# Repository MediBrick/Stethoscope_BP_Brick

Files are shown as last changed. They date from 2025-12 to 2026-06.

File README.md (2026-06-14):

# Stethoscope with Pressure Sensor

<a href="./assets/pictures/Stethoscope_Front_Closed_with_Plugins.jpg" target="_blank" style="float: right; margin-left: 20px;">
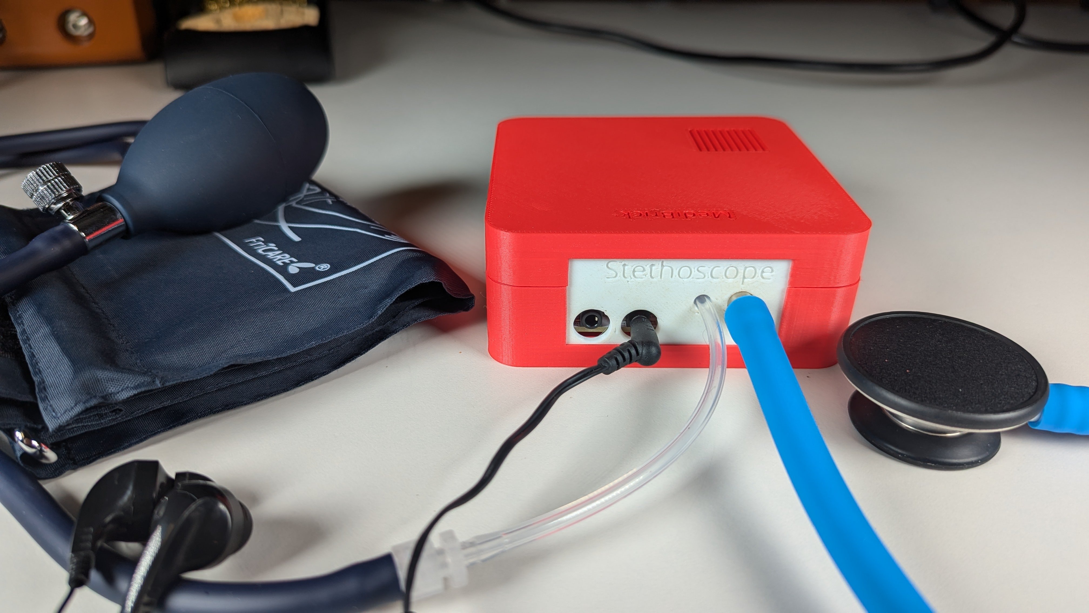
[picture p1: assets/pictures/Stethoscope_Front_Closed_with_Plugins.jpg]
  
</a>

The stethoscope and blood pressure brick consists of a sound as well as pressure recorder. For sound the I2S (Inter-Integrated Circuit Sound) bus is used to communicate with the microcontroller. This interface allows streaming and recording audio to an audio codec board. The Everest Semiconductor [ES8388 audio codec](datasheets/ES8388%20DS.pdf) was chosen because its supported by Arduino Audio Tools library and Arduino Audio Driver and because Espressif created the Lyrat Audio modules with published reference [designs](datasheets/esp32-lyrat-v4-schematic.pdf).

Sound was recorded with pui audio analog MEMS microphones [AMM-2742](datasheets/Microphone-AMM-2742-T-R.pdf) that are mounted on the printed circuit board.

However a new design is developed to use electret microphones that are attached to the flexible stethoscope tubing.

Two microphones are used where one is connected to the stethoscope and the other recording the background. An [dual differential amplifier](datasheets/opa344.pdf) is used to low pass filter and amplify the signal from the microphone, however amplification would not be needed for the ES8388 codec. Pressure is measured with a Honeywell MPR pressure sensor [MPRLS0300YG](datasheets/MPR_Pressure_HWSC_S_A0016036563_1-3073392.pdf) that convers the physiological range of 0 to 200 mm Hg.

## Costs &#36;

| Item        | Quantity at Purchase | Costs  | Source            | Cost per Brick
|---                          | ---  | ---    | ---               | ---
| Microcontroller             |  1   | $17.5  | [Adafruit](https://www.adafruit.com/product/5477)          | $17.5
| Display                     |  5   | $13    | [Amazon](https://a.co/d/1QH0Ab9)            | $3
| Button                      | 25   | $9     | [Amazon](https://a.co/d/8KAuTwC) | $0.5 
| Battery                     |  1   | $10     | [Adafruit](https://www.adafruit.com/product/258)        | $10
| PCB                         |  5   | $45.18 | PCBWay            | $9
| Parts and Assembly          |  2   | $56.55 | PCBWay            | $29
| MPRLS0300YG (pressure)      |  2   | $35    | [DigiKey](https://www.digikey.com/en/products/detail/honeywell-sensing-and-productivity-solutions/MPRLS0300YG00001B/10231660) | $17.5
| PUI AOM-5024L-HD-R (microphone)  |  2  | $4.2 | [Mouser](https://mou.sr/43AdqZY) | $8.4
| 3.5mm Audio jack stereo out(*)   | 1 | $0.9 | [Mouser](https://mou.sr/4uOWvy2) | $0.9
| 3.5mm Audio jacl mic in & stereo out(*) | 1 | $1.2 | [Mouser](https://mou.sr/4fyV8PS) | $1.2 |
| Stethoscope                 |  1   | $25    | [Amazon](https://a.co/d/7tQgoKs) | $25
| Arm Cuff                    |  1   | $17    | [Amazon](https://a.co/d/gKueGYV) | $17
| Assorted Wires              |8m    | $15    | [Amazon](https://a.co/d/58djefc) | $1
| Assorted Screws and Nuts    |100   |  $7    | Amazon            | $0.05
| Silocone Tubing             |  1   |  $9    | [Amazon](https://a.co/d/5GLJtFr) | $2
| Luer Lock female 3/32 barb  | 10   |  $9    | [Amazon](https://a.co/d/hxruOyw) | $1
| Luer Lock male 5/32 barb    | 10   |  $8    | [Amazon](https://a.co/d/c4cmtBQ) | $1
| Stainless Steel Tubing      |250mm | $10    | Amazon            | $2 |
| Assorted 3D printed parts   |      |        |                   | $3
|  **(*)** if not available at manufacturer, DIY |
| **Total with blood pressure**     |      |        |                   | **$140**
| **Total without blood pressure**  |      |        |                   | **$100**

Electronic components, excluding the pressure sensor, are $14 per board.

The pressure sensor was mounted in-house as the PCB assembly service did not have access to an inexpensive source.

## Software &#128187;

Main Program in Arduino folder:

- MediBrick_Stethoscope_BP_Microcontroller_Software: Refer to [Microcontroller_Software.md](Microcontroller_Software.md) for installation and usage instructions.

Test software is located in Arduino folder.

- MediBrick_Stethoscope_ES8388_to_CSV:
Prints the two-channel audio signal to the serial port for visualization with SerialUI application.

- MediBrick_Stethoscope_ES8388_TestSound: Creates test tone in left and right channels for headphones.

- MediBrick_Stethoscope_ES8388_to_Headphone: Plays the recorded sound to the headphone.

- MediBrick_Stethoscope_PressureTest: Test the arm cuff pressure sensor.

## Electronics Design &#128268;

<a href="KiCad/Sound_Schematic.pdf" target="_blank">
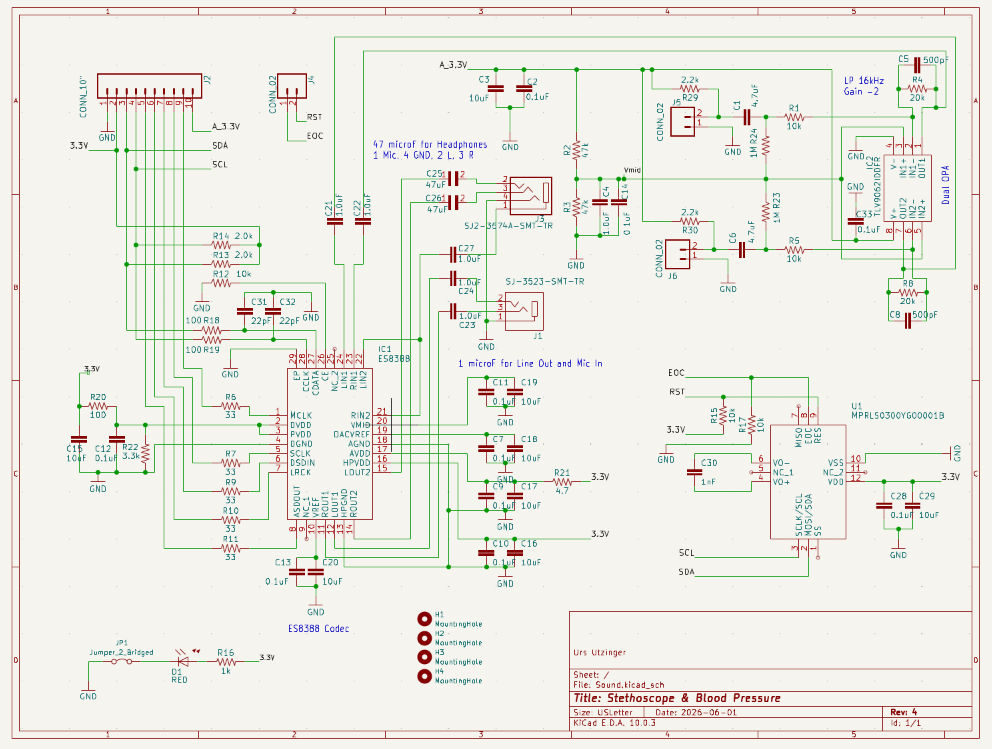
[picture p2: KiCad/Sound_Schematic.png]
  
</a>
<a href="KiCad/Sound_Layout.pdf" target="_blank">
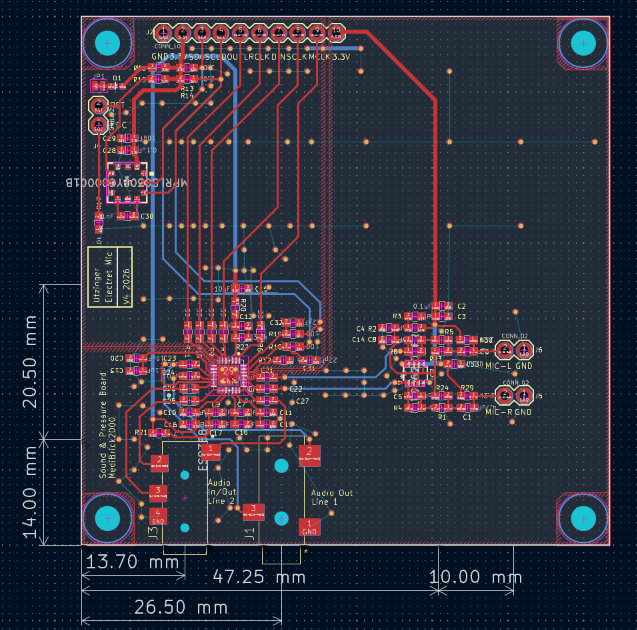
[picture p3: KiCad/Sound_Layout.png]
  
</a>

The following files are needed for PCB manufacturing and assembly at PCBWay.

- [Bill of Materials](KiCad/pcbway_production/2026-06-14-11-51-50/Sound.kicad_pcb_bom.csv)
- [Gerber Manufacturing Files](KiCad/pcbway_production/2026-06-14-11-51-50/Sound.kicad_pcb_gerber.zip)
- [Component Placement](KiCad/pcbway_production/2026-06-14-11-51-50/Sound.kicad_pcb_positions.csv)

The current design source is in [`KiCad`](KiCad/). The previous Eagle design is retained in [`Eagle`](Eagle/).

## 3D Printed Parts &#9881;
These are the links to the OnShape Design files, which you can edit and modify if you have an OnShape account (OnShape has free academic accounts).

- Microphone Housing
  - [Stethoscope Microphone Bottom](https://cad.onshape.com/documents/f23280f0a46d3d6c755669df/w/b75e085438cd92ba1b26b647/e/00c40c7437b1518e003bac9d)
  - [Stethoscope Microphone Top](https://cad.onshape.com/documents/ef2b037c38f1baa1c0b23c04/w/556b341c46d5852ab7c96559/e/758f32969c2d9c1e8976b746)

  <a href="Models/Assembly.jpg" target="_blank">
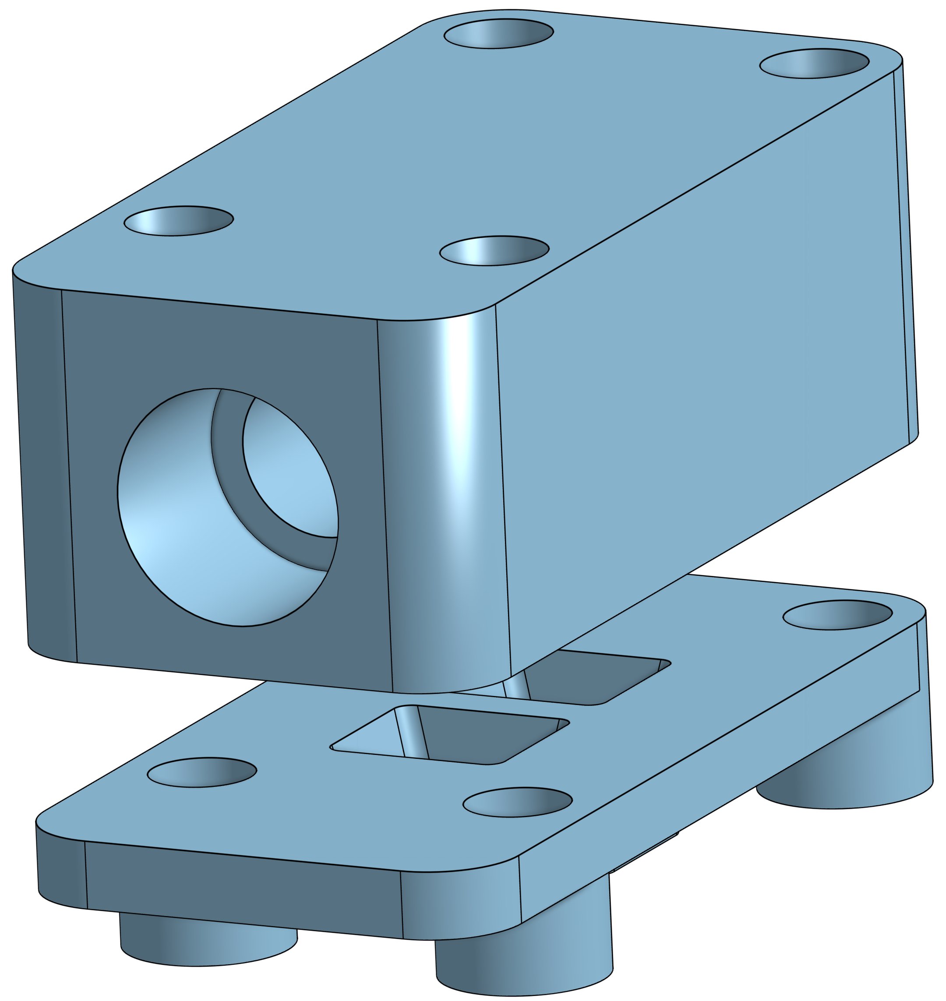
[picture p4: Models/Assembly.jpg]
    
  </a>

- MediBrick Casing (print each part separately) [This is not yet updated for new microphone]
  - [Brick Top/Board](https://cad.onshape.com/documents/ebcdcbc3e7eb802e05aa7127/w/92c7f2c4a3604ac0392e9e89/e/23d2cedb30284d3e07ce3fd7)
  - [Brick Bottom / Microcontroller](https://cad.onshape.com/documents/3fee40e68f3fb61ffdb812bb/w/65bb78ada38672d141a5d154/e/0ff82183503e2fd6c450e151)
  - [Stethoscope Interface Plate ](https://cad.onshape.com/documents/06546d5c2b6ecb0931149c5d/w/2aa54258cb58c3e795c7fea9/e/823e2851771a01788a8faacf)

## PCB Manufacturing Instructions &#128736;
When ordering at PCBWay:

Standard PCB
- Single pieces
- 70 x 70 mm
- 2 layers
- FR-4, TG 150-160
- Thickness 1.6 mm
- Minimum track width and spacing 0.15 mm
- Minimum through-hole diameter 0.25 mm
- No edge connectors
- Surface finish ENIG, 1U"
- Via process: Tenting Vias
- 1 oz Cu

Assembly Service
- Turnkey
- Single pieces
- Top side

Other Parameters
- Use the current BOM and component-placement files linked above for part counts
- Number of BGA/QFN parts: 1
- Through-hole connectors are installed separately

Customized Services and Advanced Options
- Leave as is

## Assembly Instructions &#128736;
  - [Assembly Instructions](./Assembly.md) 
 
## Audio Filters

The firmware provides adjustable high-pass and low-pass filters, software gain, and two-channel noise cancellation. These settings can be changed through the serial command interface described in [Microcontroller_Software.md](Microcontroller_Software.md).

The older offline filter-analysis utility remains available in [Compute_Filter_Coefficients.py](Compute_Filter_Coefficients.py).

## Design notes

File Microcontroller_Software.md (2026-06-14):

## Installation
Locate the "Arduino" folder in this repository. Download it to your computer. 

Install the following third-party libraries before compiling the software.

In the Arduino IDE, open `Sketch -> Include Library -> Manage Libraries...`, then search for and install each library listed below.

- [Adafruit BusIO](https://github.com/adafruit/Adafruit_BusIO)
- [Adafruit GFX Library](https://github.com/adafruit/Adafruit-GFX-Library)
- [Adafruit MAX1704X](https://github.com/adafruit/Adafruit_MAX1704X)
- [Adafruit MPRLS Library](https://github.com/adafruit/Adafruit_MPRLS)
- [Adafruit SSD1306](https://github.com/adafruit/Adafruit_SSD1306)

- Dependencies downloaded from pschatzmann, on his GitHub
  -  https://github.com/pschatzmann/arduino-audio-tools
  -  https://github.com/pschatzmann/arduino-audio-driver

Using the Arduino IDE, open the "MediBrick_Stethoscope_BP_Microcontroller_Software" folder, and flash the code to your ESP32-S3.

You will need to make sure the defaults for the wiring are correct.
It is recommended to select board configuration "USB Mode: CDC", "Upload Hardware CDC" and to enable "CDC on Boot".

## Usage Guide
The microcontroller software includes several built-in functions, including:

- Auto-shutoff after 4.5 hours
- Automatic zeroing of pressure when the MediBrick is turned on
- Blood pressure readings
- Stethoscope audio output
   - Headphone jack audio
   - SerialUI plotter

By default, the MediBrick operates in both blood pressure and stethoscope mode. In this mode, pressure readings are shown on the OLED display while stethoscope audio remains active. The stethoscope volume is set to 80% by default, and the SerialUI audio plot is disabled.

These settings can be adjusted through the internal serial menu. To access the menu guide, connect the MediBrick to the Arduino IDE through USB, open the Serial Monitor, and enter `h`. The Serial Monitor will then print the menu on the screen.

The following commands can be entered into the Serial Monitor:

**Mode selection**

| Command | Function |
|---|---|
| `p` | Pressure-only mode |
| `s` | Stethoscope-only mode |
| `b` | Both: pressure on OLED and audio active |

**Serial plot control** — while the plot is active, command responses are suppressed to keep the data stream clean

| Command | Function |
|---|---|
| `t` | Toggle audio plot on/off |
| `d` | Cycle plot decimation: 1 → 2 → 4 → 8 → 1 (reduces sample rate sent over serial) |
| `?` | Print help and turn plot off |
| `v` | Print all current settings and turn plot off |

**Settings persistence**

| Command | Function |
|---|---|
| `j` | Save current settings to flash |
| `J` | Load settings from flash and apply |

**Output (codec / headphone) volume** — range 0–100, step 6

| Command | Function |
|---|---|
| `>` | Output volume up |
| `<` | Output volume down |

**Input (microphone) volume** — nine discrete 3 dB gain levels

| Command | Function |
|---|---|
| `.` | Input volume up |
| `,` | Input volume down |

**Software gain** — range 0.5–4.0, step 0.5

| Command | Function |
|---|---|
| `+` | Software gain up |
| `-` | Software gain down |

**Low-pass filter** — step 250 Hz

| Command | Function |
|---|---|
| `L` | Low-pass cutoff frequency up |
| `l` | Low-pass cutoff frequency down |
| `K` | Low-pass filter ON |
| `k` | Low-pass filter OFF |

**High-pass filter** — step 1 Hz

| Command | Function |
|---|---|
| `H` | High-pass cutoff frequency up |
| `h` | High-pass cutoff frequency down |
| `G` | High-pass filter ON |
| `g` | High-pass filter OFF |

**Noise cancellation** (right channel minus scaled left channel)

| Command | Function |
|---|---|
| `N` | Noise cancel ON |
| `n` | Noise cancel OFF |
| `C` | Left noise scale up (step 0.05, range 0.5–1.5) |
| `c` | Left noise scale down (step 0.05, range 0.5–1.5) |

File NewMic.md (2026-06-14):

# Microphones

## Electret

- Primo EM272Z1 80 SNR -28dB 60-20000 10mm $17
- Primo EM272J  80 SNR -28dB 60-20000 10mm 600uA $17 digikey
- Primo EM258   75 SNR -32dB 60-20000 5.8mm $4.73
- Primo EM281   71 SNR -39dB 30-20000 5.8mm 450 uA $8.24 digikey
- PUI AUM-4538L 60 SNR -38dB 20-20000 9.7mm 450 uA $3 digikey

** PUI AOM-5024L-HD-R 80 SNR -24dB 20-20000 10mm (4mm opening) $4.2 **

## MEMS
differential, needs differential amp (Adafruit reference design)

- Infineon       IM70A135  70 SNR -38dB 37-20000 170uA $2.25
- TDK/InvenSense ICS-40638 63 SNR -43dB 35-20000 170uA $3.41 digikey

## Current MEMS
- PUI         AMM-2742-T-R 59 SNR -42dB 20-20000 $1.8 digikey

## Circuit for New PUI AOM-5024L-HD-R or PUI AOM-5024L-HD-F-R

### Microphone Connection
```
3.3V_Analog
  |
  2.2k
  |
  +--------- MIC+
  |
  +--------- audio out node
            |
           Ccouple 4.7 -10 uF
            |
           next stage

MIC- ---------------- AGND
```

### Direct connection (not used)
```
Electret bias node
      |
      Ccouple
   4.7–10 µF
      |
     470-1k
      |
      +-------- ES8388 LIN/RIN
      |
     1 nF (470-2.2nF)
      |
     AGND
```

### With Non Inverting OpAmp (not used)

```
3.3V_A
  |
 47k
  |
  +-----+----+- Vmid ≈ 1.65 V
  |     |    |
 47k  1-10uF 100nF
  |     |    |
 AGND   AGND AGND

Electret bias node
      |
   Ccouple
     4.7 µF
      |
      +---- 10k ----> Op Amp +IN
                    |
                    1M
                    |
                   Vmid

                 Rf
OpAmp OUT -----/\/\/\-----+
                          |
                        OpAmp -IN
                          |
                 Rg       |
Vmid ----------/\/\/\-----+

Gain = 1 + Rf/Rg

2× gain:  Rf = 10 kΩ, Rg = 10 kΩ
5× gain:  Rf = 39 kΩ, Rg = 10 kΩ
10× gain: Rf = 90 kΩ, Rg = 10 kΩ
```
## With Inverting OpAmp (used)

### Bias
```
3.3V_A
  |
 47k
  |
  +-----+----+- Vmid ≈ 1.65 V
  |     |    |
 47k  1-10uF 100nF
  |     |    |
 AGND   AGND AGND
```
### Electret microphone bias
```
3.3V_A
  |
 2.2k
  |
  +-------- Electret Mic +
  |
  +-------- Electret bias / signal node
```
### Coupling into inverting input
```
Electret bias / signal node
      |
   Ccouple
   4.7 µF
      |
      +---- Rin ----> Op Amp -IN

Op Amp +IN --------> Vmid
```

Optional bleed/startup resistor:

```
Node after Ccouple
      |
      1M
      |
     Vmid
```

### Fedback

```
                 Rf
OpAmp OUT -----/\/\/\-----+
                 ||       |
                 Cf       |
                 ||       |
                        OpAmp -IN
                          |
                 Rin      |
Mic signal ----/\/\/\-----+

Gain = -Rf / Rin

1× gain:   Rf = 10 kΩ,   Rin = 10 kΩ
2× gain:   Rf = 22 kΩ,   Rin = 10 kΩ **
5× gain:   Rf = 49.9 kΩ, Rin = 10 kΩ
10× gain:  Rf = 100 kΩ,  Rin = 10 kΩ

Rf = 10 kΩ,   Cf = 1 nF   → fc ≈ 15.9 kHz **
Rf = 22 kΩ,   Cf = 1 nF   → fc ≈ 7.2 kHz
Rf = 49.9 kΩ, Cf = 470 pF → fc ≈ 6.8 kHz
```

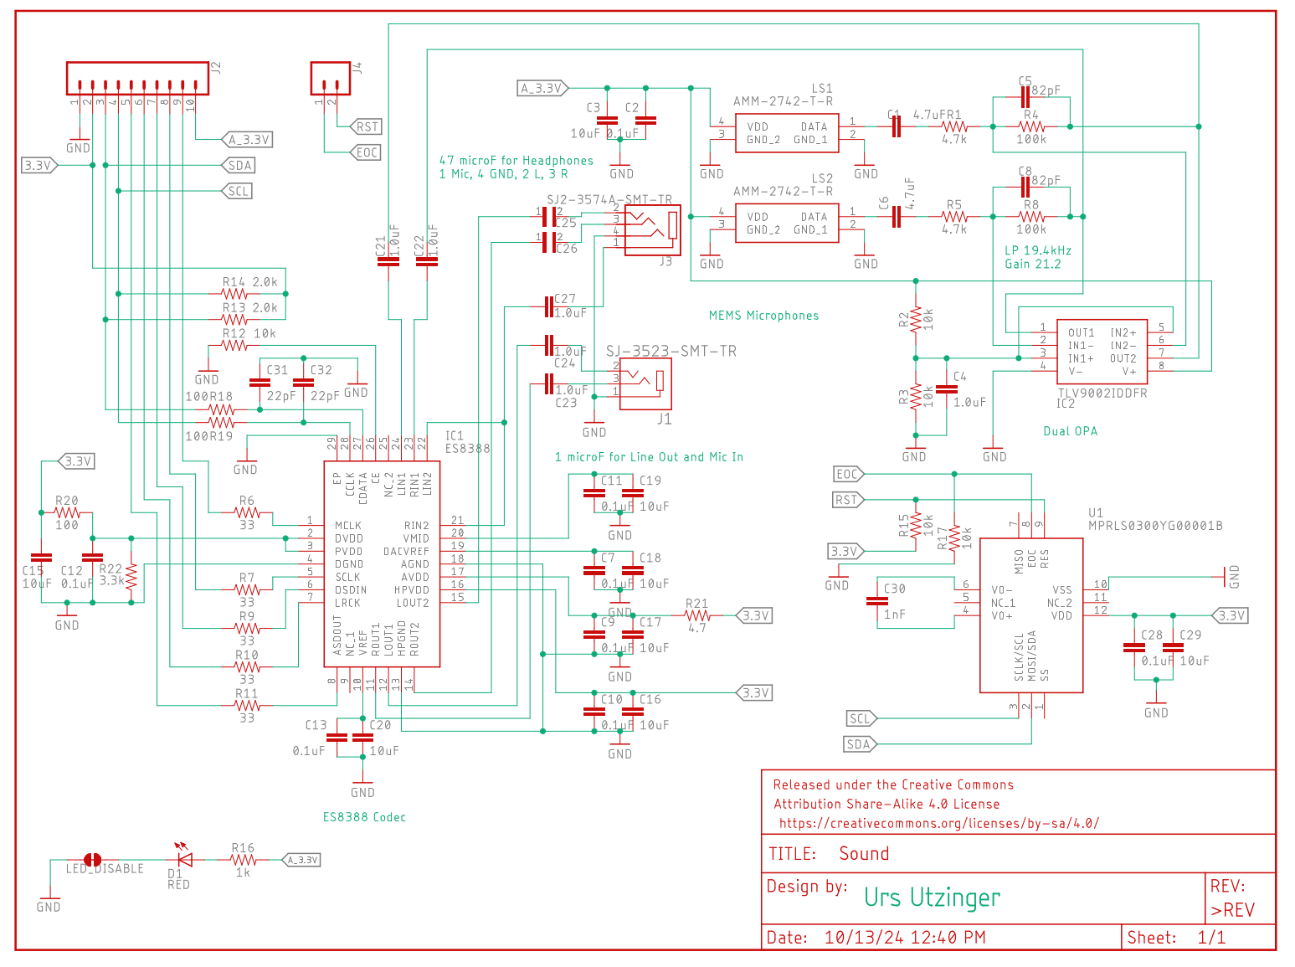
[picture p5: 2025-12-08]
Eagle/Sound_schematic.png

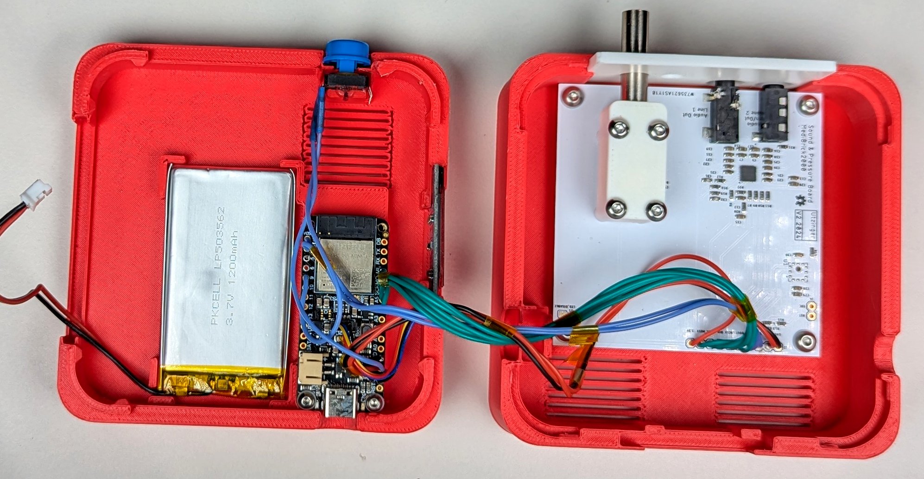
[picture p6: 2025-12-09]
assets/pictures/Stethoscope_Top_Open_without_Plugins.jpg

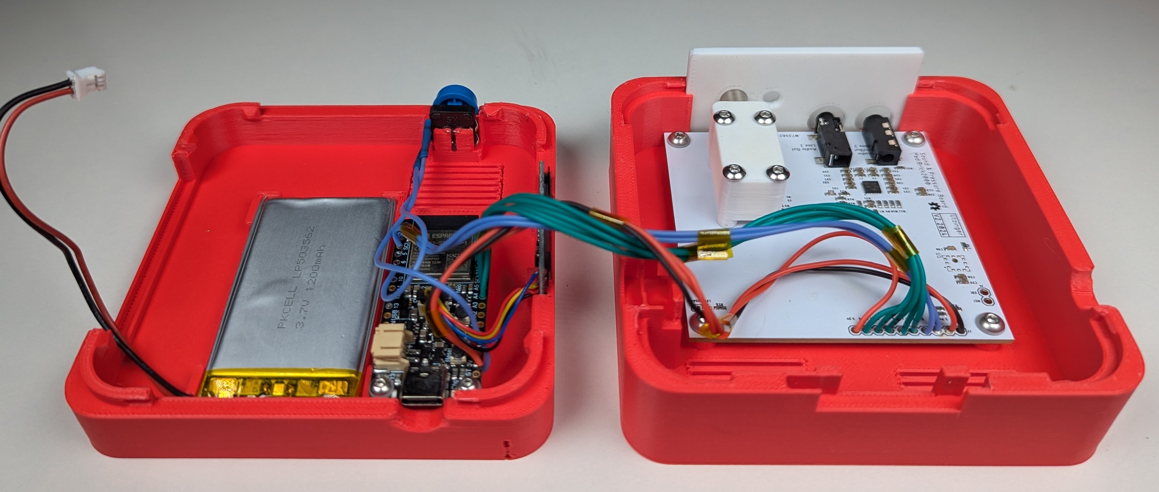
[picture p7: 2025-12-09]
assets/pictures/Stethoscope_Front_Open_without_Plugins.jpg

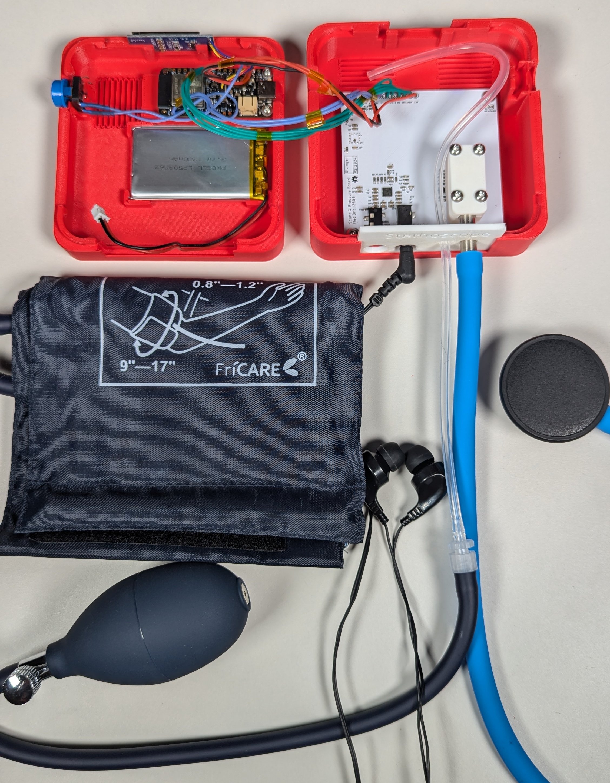
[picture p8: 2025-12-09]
assets/pictures/Stethoscope_Top_Open_with_Plugins_2.jpg

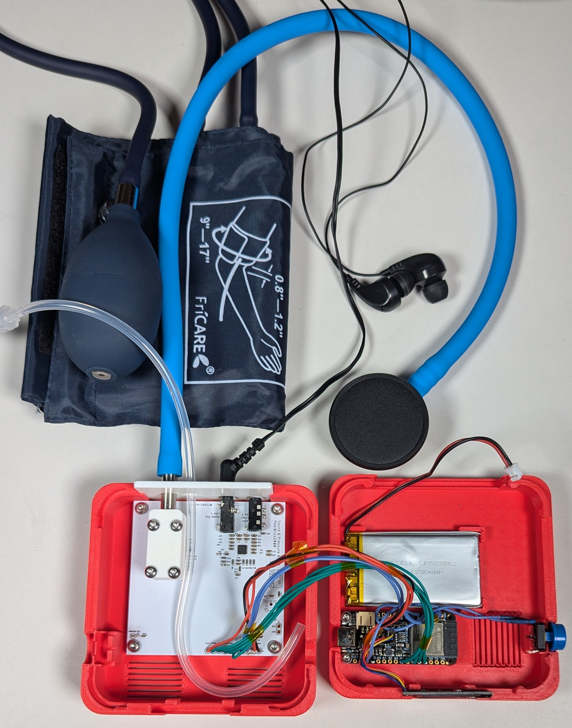
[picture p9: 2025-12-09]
assets/pictures/Stethoscope_Top_Open_with_Plugins.jpg

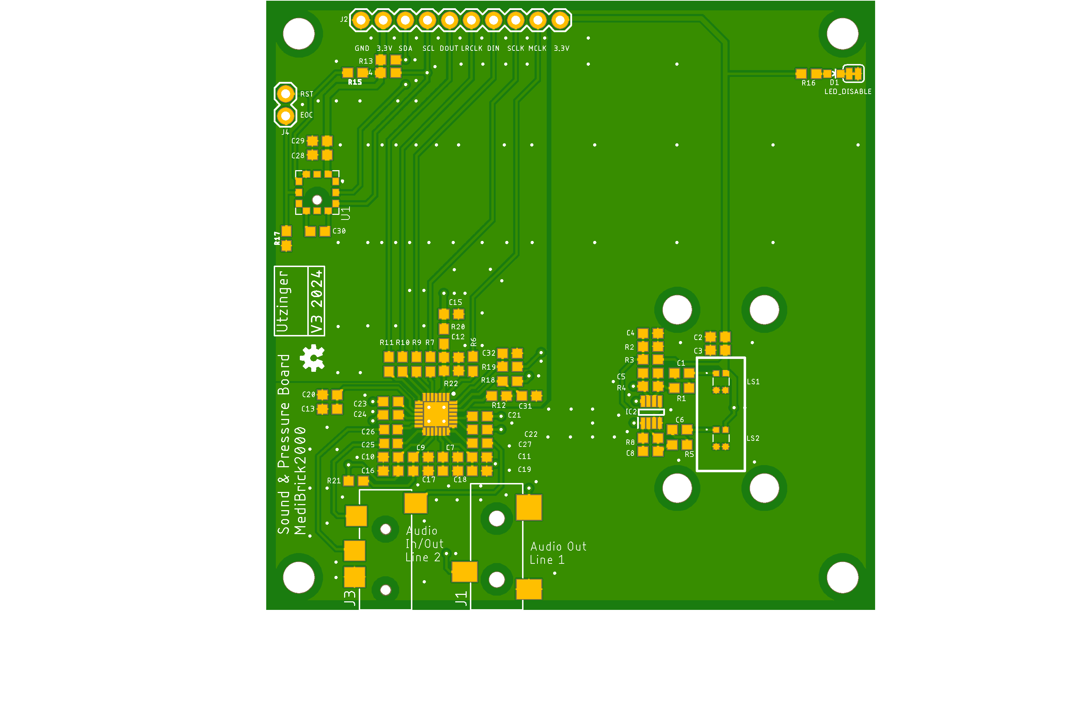
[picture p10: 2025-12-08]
Eagle/Sound_top.png

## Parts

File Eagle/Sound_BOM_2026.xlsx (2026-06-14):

Based on PCBWay Bom Quotation
Item # | *Designator | *Qty | Manufacturer | *Mfg Part # | Description / Value | Vendor Part # | *Package/Footprint | Mounting Type | Your Instructions / Notes | *Unit Price(2 sets) | *Total | *Delivery Time | *Actual Purchase Mfg Part # | Customer Reply
1 | C2, C7, C9, C10, C11, C12, C13, C28 | 8 | muRata | GRM188R71H104KA93D | 0.1uF | C77055 | 0603 | SMD |  |  | $0.000
2 | C4, C21, C22, C23, C24, C27 | 6 | muRata | GCM188R71E105KA64D | 1.0uF | C85862 | 0603 | SMD |  |  | $0.000
3 | C3, C15, C16, C17, C18, C19, C20, C29 | 8 | muRata | GRM188R61A106KE69D | 10uF | C77044 | 0603 | SMD |  |  | $0.000
4 | C1, C6 | 2 | muRata | GRM188R61E475KE11D | 4.7uF | C90057 | 0603 | SMD |  |  | $0.000
5 | C5, C8 | 2 | muRata | GCM1885C2A181JA16D | 180pF | C440148 | 0603 | SMD |  |  | $0.000
6 | C25, C26 | 2 | muRata | GRM188R60J476ME15D | 47uF | C140782 | 0603 | SMD |  |  | $0.000
7 | C30 | 1 | muRata | GRM1885C1H102JA01D | 1nF | C77026 | 0603 | SMD |  |  | $0.000
8 | C31, C32 | 2 | muRata | GCG1885G1H220JA01D | 22pF | C3884601 | 0603 | SMD |  |  | $0.000
9 | R1, R5 | 2 | YAGEO | RC0603FR-074K7L | 4.7k | C99782 | 0603 | SMD |  |  | $0.000
10 | R2, R3, R12, R15, R17 | 5 | YAGEO | RT0603BRD0710KL | 10k | C95204 | 0603 | SMD |  |  | $0.000
11 | R4, R8 | 2 | YAGEO | RC0603JR-0747KL | 47k | C127447 | 0603 | SMD |  |  | $0.000
12 | R6, R7, R9, R10, R11 | 5 | YAGEO | RC0603JR-0733RL | 33 | C108407 | 0603 | SMD |  |  | $0.000
13 | R13, R14 | 2 | YAGEO | RT0603BRB072KL | 2k | C326555 | 0603 | SMD |  |  | $0.000 |  | RC0603FR-072KL
14 | R16 | 1 | YAGEO | RT0603BRD071KL | 1k | C110776 | 0603 | SMD |  |  | $0.000
15 | R18, R19, R20 | 3 | YAGEO | RT0603BRD07100RL | 100 | C122970 | 0603 | SMD |  |  | $0.000
16 | R21 | 1 | YAGEO | RT0603DRE074R7L | 4.7 | C863140 | 0603 | SMD |  |  | $0.000
17 | R22 | 1 | YAGEO | RT0603BRB073K3L | 3.3k | C860369 | 0603 | SMD |  |  | $0.000
18 | LS1, LS2 | 2 | PUI Audio, Inc. | AMM-2742-T-R | AMM-2742-T-R, MEMS Microphones |  | 0603 | SMD | https://mou.sr/4uW6BxI |  | $0.000 | 7-10 Workdays
19 | IC1 | 1 | Everest-semi(Everest Semiconductor) | ES8388 | ES8388 | C365736 | QFN-28-EP(4x4) | SMD |  |  | $0.000
20 | D1 | 1 | XINGLIGHT | XL-1608UBC-04 | Blue LED | C965807 | 0603 | SMD |  |  | $0.000
21 | J1 | 1 | CUI Devices | SJ-3523-SMT-TR | SJ-3523-SMT-TR, 3.5mm Audio Jack | C4991872 |  | SMD | https://mou.sr/4uOWvy2 |  | $0.000
22 | J3 | 1 | CUI Devices | SJ2-3574A-SMT-TR | SJ2-3574A-SMT-TR, 3.5mm Audio Jack with microphone | C4991637 |  | SMD | https://mou.sr/4fyV8PS |  | $0.000 | 7-10 Workdays
23 | IC2 | 1 | Texas Instruments | TLV9062IDDFR | 10 MHz, RRIO, CMOS operational amplifier | C2867884 | TSOT-23-8 | SMD |  |  | $0.000 | 7-10 Workdays
 |  |  |  |  |  |  |  |  |  | Component Cost | $0.00

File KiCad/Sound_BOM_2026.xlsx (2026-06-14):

Item # | *Designator | *Qty | Manufacturer | *Mfg Part # | Description / Value | Vendor Part # | *Package/Footprint | Mounting Type | Your Instructions / Notes | *Unit Price(2 sets) | *Total | *Delivery Time | *Actual Purchase Mfg Part # | Customer Reply
1 | C2, C7, C9, C10, C11, C12, C13, C14, C28, C33 | 10 | muRata | GRM188R71H104KA93D | 100nF | C77055 | 0603 | SMD |  |  | $0.000
2 | C4, C21, C22, C23, C24, C27 | 6 | muRata | GCM188R71E105KA64D | 1.0uF | C85862 | 0603 | SMD |  |  | $0.000
3 | C3, C15, C16, C17, C18, C19, C20, C29 | 8 | muRata | GRM188R61A106KE69D | 10uF | C77044 | 0603 | SMD |  |  | $0.000
4 | C1, C6 | 2 | muRata | GRM188R61E475KE11D | 4.7uF | C90057 | 0603 | SMD |  |  | $0.000
5 | C5, C8 | 2 | YAEGO | CC0603JRNPO9BN501 | 500pF | C3879676 | 0603 | SMD |  |  | $0.000
6 | C25, C26 | 2 | muRata | GRM188R60J476ME15D | 47uF | C140782 | 0603 | SMD |  |  | $0.000
7 | C30 | 1 | muRata | GRM1885C1H102JA01D | 1nF | C77026 | 0603 | SMD |  |  | $0.000
8 | C31, C32 | 2 | muRata | GCG1885G1H220JA01D | 22pF | C3884601 | 0603 | SMD |  |  | $0.000
9 | R1, R5, R12, R15, R17 | 5 | YAGEO | RT0603BRD0710KL | 10k | C95204 | 0603 | SMD |  |  | $0.000
10 | R2, R3 | 2 | YAGEO | RC0603JR-0747KL | 47k | C127447 | 0603 | SMD |  |  | $0.000
11 | R4, R8 | 2 | YAGEO | RT0603BRD0720KL | 20k | C723637 | 0603 | SMD |  |  | $0.000
12 | R6, R7, R9, R10, R11 | 5 | YAGEO | RC0603JR-0733RL | 33 | C108407 | 0603 | SMD |  |  | $0.000
13 | R13, R14 | 2 | YAGEO | RT0603BRB072KL | 2k | C326555 | 0603 | SMD |  |  | $0.000 |  | RC0603FR-072KL
14 | R16 | 1 | YAGEO | RT0603BRD071KL | 1k | C110776 | 0603 | SMD |  |  | $0.000
15 | R18, R19, R20 | 3 | YAGEO | RT0603BRD07100RL | 100 | C122970 | 0603 | SMD |  |  | $0.000
16 | R21 | 1 | YAGEO | RT0603DRE074R7L | 4.7 | C863140 | 0603 | SMD |  |  | $0.000
17 | R22 | 1 | YAGEO | RT0603BRB073K3L | 3.3k | C860369 | 0603 | SMD |  |  | $0.000
18 | R23, R24 | 2 | YAGEO | RC0603FR-071ML | 1M | C105578 | 0603 | SMD
19 | R29, R30 | 2 | YAGEO | AC0603FR-072K2L | 2.2k | C125931 | 0603 | SMD
20 | IC1 | 1 | Everest-semi(Everest Semiconductor) | ES8388 | ES8388 | C365736 | QFN-28-EP(4x4) | SMD |  |  | $0.000
21 | D1 | 1 | XINGLIGHT | XL-1608UBC-04 | Blue LED | C965807 | 0603 | SMD |  |  | $0.000
22 | J1 | 1 | CUI Devices | SJ-3523-SMT-TR | SJ-3523-SMT-TR, 3.5mm Audio Jack | C4991872 | Custom | SMD | https://mou.sr/4uOWvy2 |  | $0.000
23 | J2 | 1 |  | Connector | 1x10 | Do not populate
24 | J3 | 1 | CUI Devices | SJ2-3574A-SMT-TR | SJ2-3574A-SMT-TR, 3.5mm Audio Jack with microphone | C4991637 | Custom | SMD | https://mou.sr/4fyV8PS |  | $0.000 | 7-10 Workdays
25 | J4, J5, J6 | 3 |  | Connector | 1x2 | Do not populate
26 | JP1 | 1 |  | Jumper NC |  | Do not populate
27 | IC2 | 1 | Texas Instruments | TLV9062IDDFR | 10 MHz, RRIO, CMOS operational amplifier | C2867884 | TSOT-23-8 | SMD |  |  | $0.000 | 7-10 Workdays
 |  |  |  |  |  |  |  |  |  | Component Cost | $0.00
 |  | 69

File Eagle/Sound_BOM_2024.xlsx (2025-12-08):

Item # | Designator | Qty | Manufacturer | Mfg Part # | LCSC Part# | U.S. Distributor | Description / Value | *Package/Footprint | Mounting Type | Your Instructions / Notes
1 | C2, C7, C9, C10, C11, C12, C13, C28 | 8 | Samsung Electro-Mechanics (https://www.lcsc.com/brand-detail/254.html) | CL10B104KA8NNNC (https://www.lcsc.com/product-detail/Multilayer-Ceramic-Capacitors-MLCC-SMD-SMT_Samsung-Electro-Mechanics-CL10B104KA8NNNC_C1590.html) | C1590 (https://www.lcsc.com/product-detail/Multilayer-Ceramic-Capacitors-MLCC-SMD-SMT_Samsung-Electro-Mechanics-CL10B104KA8NNNC_C1590.html) |  | 0.1uF | 0603 | SMD
2 | C4, C21, C22, C23, C24, C27 | 6 | Samsung Electro-Mechanics (https://www.lcsc.com/brand-detail/254.html) | CL10A105KA8NNNC (https://www.lcsc.com/product-detail/Multilayer-Ceramic-Capacitors-MLCC-SMD-SMT_Samsung-Electro-Mechanics-CL10A105KA8NNNC_C5673.html) | C5673 (https://www.lcsc.com/product-detail/Multilayer-Ceramic-Capacitors-MLCC-SMD-SMT_Samsung-Electro-Mechanics-CL10A105KA8NNNC_C5673.html) |  | 1.0uF | 0603 | SMD
3 | C3, C15, C16, C17, C18, C19, C20, C29 | 8 | Samsung Electro-Mechanics (https://www.lcsc.com/brand-detail/254.html) | CL10A106MA8NRNC (https://www.lcsc.com/product-detail/Multilayer-Ceramic-Capacitors-MLCC-SMD-SMT_Samsung-Electro-Mechanics-CL10A106MA8NRNC_C96446.html) | C96446 (https://www.lcsc.com/product-detail/Multilayer-Ceramic-Capacitors-MLCC-SMD-SMT_Samsung-Electro-Mechanics-CL10A106MA8NRNC_C96446.html) |  | 10uF | 0603 | SMD
4 | C1, C6 | 2 | Samsung Electro-Mechanics (https://www.lcsc.com/brand-detail/254.html) | CL10A475KA8NQNC (https://www.lcsc.com/product-detail/Multilayer-Ceramic-Capacitors-MLCC-SMD-SMT_Samsung-Electro-Mechanics-CL10A475KA8NQNC_C69335.html) | C69335 (https://www.lcsc.com/product-detail/Multilayer-Ceramic-Capacitors-MLCC-SMD-SMT_Samsung-Electro-Mechanics-CL10A475KA8NQNC_C69335.html) |  | 4.7uF | 0603 | SMD
5 | C5, C8 | 2 | Samsung Electro-Mechanics (https://www.lcsc.com/brand-detail/254.html) | CL10C102JB8NNNC (https://www.lcsc.com/product-detail/Multilayer-Ceramic-Capacitors-MLCC-SMD-SMT_Samsung-Electro-Mechanics-CL10C102JB8NNNC_C163508.html) | C163508 (https://www.lcsc.com/product-detail/Multilayer-Ceramic-Capacitors-MLCC-SMD-SMT_Samsung-Electro-Mechanics-CL10C102JB8NNNC_C163508.html) |  | 1000pF | 0603 | SMD | Was 82.pF in version 2
6 | C25, C26 | 2 | Samsung Electro-Mechanics (https://www.lcsc.com/brand-detail/254.html) | CL10A476MQ8QRNC (https://www.lcsc.com/product-detail/Multilayer-Ceramic-Capacitors-MLCC-SMD-SMT_Samsung-Electro-Mechanics-CL10A476MQ8QRNC_C730416.html) | C730416 (https://www.lcsc.com/product-detail/Multilayer-Ceramic-Capacitors-MLCC-SMD-SMT_Samsung-Electro-Mechanics-CL10A476MQ8QRNC_C730416.html) |  | 47uF | 0603 | SMD
7 | C30 | 1 | Samsung Electro-Mechanics (https://www.lcsc.com/brand-detail/254.html) | CL10B102KB8NNNC (https://www.lcsc.com/product-detail/Multilayer-Ceramic-Capacitors-MLCC-SMD-SMT_Samsung-Electro-Mechanics-CL10B102KB8NNNC_C1588.html) | C1588 (https://www.lcsc.com/product-detail/Multilayer-Ceramic-Capacitors-MLCC-SMD-SMT_Samsung-Electro-Mechanics-CL10B102KB8NNNC_C1588.html) |  | 1nF | 0603 | SMD
8 | C31, C32 | 2 | Samsung Electro-Mechanics (https://www.lcsc.com/brand-detail/254.html) | CL10C220JB8NNNC (https://www.lcsc.com/product-detail/Multilayer-Ceramic-Capacitors-MLCC-SMD-SMT_Samsung-Electro-Mechanics-CL10C220JB8NNNC_C1653.html) | C1653 (https://www.lcsc.com/product-detail/Multilayer-Ceramic-Capacitors-MLCC-SMD-SMT_Samsung-Electro-Mechanics-CL10C220JB8NNNC_C1653.html) |  | 22pF | 0603 | SMD
9 | R1, R5 | 2 | YAGEO (https://www.lcsc.com/brand-detail/396.html) | RC0603FR-074K7L (https://www.lcsc.com/product-detail/Chip-Resistor-Surface-Mount_YAGEO-RC0603FR-074K7L_C99782.html) | C99782 (https://www.lcsc.com/product-detail/Chip-Resistor-Surface-Mount_YAGEO-RC0603FR-074K7L_C99782.html) |  | 4.7k | 0603 | SMD
10 | R2, R3, R12, R15, R17 | 5 | YAGEO (https://www.lcsc.com/brand-detail/396.html) | RC0603FR-0710KL (https://www.lcsc.com/product-detail/Chip-Resistor-Surface-Mount_YAGEO-RC0603FR-0710KL_C98220.html) | C98220 (https://www.lcsc.com/product-detail/Chip-Resistor-Surface-Mount_YAGEO-RC0603FR-0710KL_C98220.html) |  | 10k | 0603 | SMD
11 | R4, R8 | 2 | YAGEO (https://www.lcsc.com/brand-detail/396.html) | RC0603FR-078K2L (https://www.lcsc.com/product-detail/Chip-Resistor-Surface-Mount_YAGEO-RC0603FR-078K2L_C114637.html) | C114637 (https://www.lcsc.com/product-detail/Chip-Resistor-Surface-Mount_YAGEO-RC0603FR-078K2L_C114637.html) |  | 8.2k | 0603 | SMD | Was 100k in version 2
12 | R6, R7, R9, R10, R11 | 5 | YAGEO (https://www.lcsc.com/brand-detail/396.html) | RC0603FR-0733RL (https://www.lcsc.com/product-detail/Chip-Resistor-Surface-Mount_YAGEO-RC0603FR-0733RL_C108661.html) | C108661 (https://www.lcsc.com/product-detail/Chip-Resistor-Surface-Mount_YAGEO-RC0603FR-0733RL_C108661.html) |  | 33 | 0603 | SMD
13 | R13, R14 | 2 | YAGEO (https://www.lcsc.com/brand-detail/396.html) | RC0603FR-072KL (https://www.lcsc.com/product-detail/Chip-Resistor-Surface-Mount_YAGEO-RC0603FR-072KL_C105576.html) | C105576 (https://www.lcsc.com/product-detail/Chip-Resistor-Surface-Mount_YAGEO-RC0603FR-072KL_C105576.html) |  | 2k | 0603 | SMD
14 | R16 | 1 | YAGEO (https://www.lcsc.com/brand-detail/396.html) | RC0603FR-071KL (https://www.lcsc.com/product-detail/Chip-Resistor-Surface-Mount_YAGEO-RC0603FR-071KL_C22548.html) | C22548 (https://www.lcsc.com/product-detail/Chip-Resistor-Surface-Mount_YAGEO-RC0603FR-071KL_C22548.html) |  | 1k | 0603 | SMD
15 | R18, R19, R20 | 3 | YAGEO (https://www.lcsc.com/brand-detail/396.html) | RC0603FR-07100RL (https://www.lcsc.com/product-detail/Chip-Resistor-Surface-Mount_YAGEO-RC0603FR-07100RL_C105588.html) | C105588 (https://www.lcsc.com/product-detail/Chip-Resistor-Surface-Mount_YAGEO-RC0603FR-07100RL_C105588.html) |  | 100 | 0603 | SMD
16 | R21 | 1 | YAGEO (https://www.lcsc.com/brand-detail/396.html) | RC0603FR-074R7L (https://www.lcsc.com/product-detail/Chip-Resistor-Surface-Mount_YAGEO-RC0603FR-074R7L_C137705.html) | C137705 (https://www.lcsc.com/product-detail/Chip-Resistor-Surface-Mount_YAGEO-RC0603FR-074R7L_C137705.html) |  | 4.7 | 0603 | SMD
17 | R22 | 1 | YAGEO (https://www.lcsc.com/brand-detail/396.html) | RC0603FR-073K3L (https://www.lcsc.com/product-detail/Chip-Resistor-Surface-Mount_YAGEO-RC0603FR-073K3L_C108078.html) | C108078 (https://www.lcsc.com/product-detail/Chip-Resistor-Surface-Mount_YAGEO-RC0603FR-073K3L_C108078.html) |  | 3.3k | 0603 | SMD
18 | LS1, LS2 | 2 | PUI Audio, Inc. (https://www.lcsc.com/brand-detail/13209.html) | AMM-2742-T-R (https://www.lcsc.com/product-detail/MEMS-Microphones_PUI-Audio-Inc-AMM-2742-T-R_C3171735.html) | C3171735 (https://www.lcsc.com/product-detail/MEMS-Microphones_PUI-Audio-Inc-AMM-2742-T-R_C3171735.html) | https://www.mouser.com/ProductDetail/PUI-Audio/AMM-2742-T-R?qs=zhx2xqPtQQyJoGop0O%252BpMA%3D%3D | AMM-2742-T-R, MEMS Microphones | 0603 | SMD
19 | IC1 | 1 | Everest-semi(Everest Semiconductor) (https://www.lcsc.com/brand-detail/11902.html) | ES8388 (https://www.lcsc.com/product-detail/ADCs-DACs-Special-Purpose_Everest-semi-Everest-Semiconductor-ES8388_C365736.html) | C365736 (https://www.lcsc.com/product-detail/ADCs-DACs-Special-Purpose_Everest-semi-Everest-Semiconductor-ES8388_C365736.html) |  | ES8388 | QFN-28-EP(4x4) | SMD
20 | D1 | 1 | XINGLIGHT | XL-1608UBC-04 (https://www.lcsc.com/product-detail/Light-Emitting-Diodes-LED_XINGLIGHT-XL-1608UBC-04_C965807.html) | C965807 (https://www.lcsc.com/product-detail/Light-Emitting-Diodes-LED_XINGLIGHT-XL-1608UBC-04_C965807.html) |  | Blue LED | 0603 | SMD
21 | J1 | 1 | CUI Devices (https://www.lcsc.com/brand-detail/15740.html) | SJ-3523-SMT-TR (https://www.lcsc.com/product-detail/Audio-Connector-Headphone_CUI-Devices-SJ-3523-SMT-TR_C4991872.html) |  | https://www.mouser.com/ProductDetail/CUI-Devices/SJ-3523-SMT-TR?qs=WyjlAZoYn51zOHzJ3r4ZRA%3D%3D | SJ-3523-SMT-TR, 3.5mm Audio Jack |  | SMD
22 | J3 | 1 | CUI Devices (https://www.lcsc.com/brand-detail/15740.html) | SJ2-3574A-SMT-TR (https://www.lcsc.com/product-detail/Audio-Connector-Headphone_CUI-Devices-SJ2-3574A-SMT-TR_C4991637.html) |  | https://www.mouser.com/ProductDetail/CUI-Devices/SJ2-3574A-SMT-TR?qs=DXv0QSHKF4zeQKpjIMxQnA%3D%3D | SJ2-3574A-SMT-TR, 3.5mm Audio Jack with microphone |  | SMD
23 | IC2 | 1 | Texas Instruments (https://www.lcsc.com/brand-detail/100.html) | TLV9002IDDFR (https://www.lcsc.com/product-detail/Operational-Amplifier_Texas-Instruments-TLV9002IDDFR_C2862620.html) | C2862620 (https://www.lcsc.com/product-detail/Operational-Amplifier_Texas-Instruments-TLV9002IDDFR_C2862620.html) |  | TLV9002IDDFR, Dual OpAmp | TSOT-23-8 | SMD
 |  | 60
 | Resistors | 22
 | Capacitors | 31

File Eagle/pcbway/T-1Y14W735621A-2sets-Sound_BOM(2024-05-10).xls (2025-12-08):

PCBWay Bom Quotation, Product No.:T-1Y14W735621A
Item # | *Designator | *Qty | Manufacturer | *Mfg Part # | Description / Value | Vendor Part # | *Package/Footprint | Mounting Type | Your Instructions / Notes | *Unit Price(2 sets) | *Total | *Delivery Time | *PCBWay Note | Customer Reply
1 | C2, C7, C9, C10, C11, C12, C13, C28 | 8 | Samsung Electro-Mechanics | CL10B104KA8NNNC | 0.1uF | C1590 | 0603 | SMD |  | $0.024 | $0.384
2 | C4, C21, C22, C23, C24, C27 | 6 | Samsung Electro-Mechanics | CL10A105KA8NNNC | 1.0uF | C5673 | 0603 | SMD |  | $0.042 | $0.504
3 | C3, C14, C15, C16, C17, C18, C19, C20, C29 | 9 | Samsung Electro-Mechanics | CL10A106MA8NRNC | 10uF | C96446 | 0603 | SMD |  | $0.042 | $0.756
4 | C1, C6 | 2 | Samsung Electro-Mechanics | CL10A475KA8NQNC | 4.7uF | C69335 | 0603 | SMD |  | $0.063 | $0.252
5 | C5, C8 | 2 | Samsung Electro-Mechanics | CL10C270JB81PNC | 27pF | C346211 | 0603 | SMD |  | $0.063 | $0.252
6 | C25, C26 | 2 | Samsung Electro-Mechanics | CL10A476MQ8QRNC | 47uF | C730416 | 0603 | SMD |  | $0.258 | $1.032
7 | C30 | 1 | Samsung Electro-Mechanics | CL10B102KB8NNNC | 1nF | C1588 | 0603 | SMD |  | $0.126 | $0.252
8 | R1, R5 | 2 | YAGEO | RC0603FR-074K7L | 4.7k | C99782 | 0603 | SMD |  | $0.035 | $0.140
9 | R2, R3, R12, R13, R14 | 5 | YAGEO | RC0603FR-0710KL | 10k | C98220 | 0603 | SMD |  | $0.013 | $0.130
10 | R4, R8 | 2 | YAGEO | RC0603FR-07300KL | 300k | C114667 | 0603 | SMD |  | $0.039 | $0.156
11 | R6, R7, R9, R10, R11, R15, R17 | 7 | YAGEO | RC0603FR-0733RL | 33 | C108661 | 0603 | SMD |  | $0.011 | $0.154
12 | R16 | 1 | YAGEO | RC0603FR-071KL | 1k | C22548 | 0603 | SMD |  | $0.065 | $0.130
13 | LS1, LS2 | 2 | PUI Audio, Inc. | AMM-2742-T-R | AMM-2742-T-R, MEMS Microphones | C3171735 | 0603 | SMD | https://www.mouser.com/ProductDetail/PUI-Audio/AMM-2742-T-R?qs=zhx2xqPtQQyJoGop0O%252BpMA%3D%3D | $2.537 | $10.148 | 7-10 Workdays | Only 270pcs total in stock, please confirm ASAP.
14 | IC1 | 1 | Everest-semi(Everest Semiconductor) | ES8388 | ES8388 | C365736 | QFN-28-EP(4x4) | SMD |  | $1.464 | $2.928
15 | U1 | 1 | Honeywell | MPRLS0300YG00001BB | MPRLS0300YG00001B |  |  | SMD | https://www.mouser.com/ProductDetail/Honeywell/MPRLS0300YG00001B?qs=MLItCLRbWszf0bln%252B%2FiVCQ%3D%3D | $67.882 | $135.764 | 7-10 Workdays | Only 400pcs total in stock, please confirm ASAP.
16 | D1 | 1 | XINGLIGHT | XL-1608UBC-04 | Blue LED | C965807 | 0603 | SMD |  | $0.238 | $0.476
17 | J1 | 1 | CUI Devices | SJ-3523-SMT-TR | SJ-3523-SMT-TR, 3.5mm Audio Jack |  |  | SMD | https://www.mouser.com/ProductDetail/CUI-Devices/SJ-3523-SMT-TR?qs=WyjlAZoYn51zOHzJ3r4ZRA%3D%3D | $2.113 | $4.226
18 | J3 | 1 | CUI Devices | SJ2-3574A-SMT-TR | SJ2-3574A-SMT-TR, 3.5mm Audio Jack with microphone |  |  | SMD | https://www.mouser.com/ProductDetail/CUI-Devices/SJ2-3574A-SMT-TR?qs=DXv0QSHKF4zeQKpjIMxQnA%3D%3D | $1.916 | $3.832 | 7-10 Workdays
19 | IC2 | 1 | Texas Instruments | TLV9002IDDFR | TLV9002IDDFR, Dual OpAmp | C2862620 | TSOT-23-8 | SMD |  | $1.057 | $2.114
 |  |  |  |  |  |  |  |  |  | Component Cost | $163.63

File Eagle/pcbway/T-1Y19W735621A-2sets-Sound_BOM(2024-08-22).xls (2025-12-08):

PCBWay Bom Quotation, Product No.:T-1Y19W735621A
Item # | *Designator | *Qty | Manufacturer | *Mfg Part # | Description / Value | Vendor Part # | *Package/Footprint | Mounting Type | Your Instructions / Notes | *Unit Price(2 sets) | *Total | *Delivery Time | *Actual Purchase Mfg Part # | Customer Reply
1 | C2, C7, C9, C10, C11, C12, C13, C28 | 8 | Samsung Electro-Mechanics | CL10B104KA8NNNC | 0.1uF | C1590 | 0603 | SMD |  | $0.026 | $0.416
2 | C4, C21, C22, C23, C24, C27 | 6 | Samsung Electro-Mechanics | CL10A105KA8NNNC | 1.0uF | C5673 | 0603 | SMD |  | $0.010 | $0.120
3 | C3, C15, C16, C17, C18, C19, C20, C29 | 8 | Samsung Electro-Mechanics | CL10A106MA8NRNC | 10uF | C96446 | 0603 | SMD |  | $0.041 | $0.656
4 | C1, C6 | 2 | Samsung Electro-Mechanics | CL10A475KA8NQNC | 4.7uF | C69335 | 0603 | SMD |  | $0.063 | $0.252
5 | C5, C8 | 2 | Samsung Electro-Mechanics | CL10C820JB81PNC | 82pF | C472802 | 0603 | SMD |  | $0.063 | $0.252
6 | C25, C26 | 2 | Samsung Electro-Mechanics | CL10A476MQ8QRNC | 47uF | C730416 | 0603 | SMD |  | $0.184 | $0.736
7 | C30 | 1 | Samsung Electro-Mechanics | CL10B102KB8NNNC | 1nF | C1588 | 0603 | SMD |  | $0.126 | $0.252
8 | C31, C32 | 2 | Samsung Electro-Mechanics | CL10C220JB8NNNC | 22pF | C1653 | 0603 | SMD |  | $0.063 | $0.252
9 | R1, R5 | 2 | YAGEO | RC0603FR-074K7L | 4.7k | C99782 | 0603 | SMD |  | $0.053 | $0.212
10 | R2, R3, R12, R15, R17 | 5 | YAGEO | RC0603FR-0710KL | 10k | C98220 | 0603 | SMD |  | $0.013 | $0.130
11 | R4, R8 | 2 | YAGEO | RC0603FR-07100KL | 100k | C14675 | 0603 | SMD |  | $0.031 | $0.124
12 | R6, R7, R9, R10, R11 | 5 | YAGEO | RC0603FR-0733RL | 33 | C108661 | 0603 | SMD |  | $0.016 | $0.160
13 | R13, R14 | 2 | YAGEO | RC0603FR-0710KL | 2k | C98220 | 0603 | SMD |  | $0.038 | $0.152 |  | RC0603FR-072KL
14 | R16 | 1 | YAGEO | RC0603FR-071KL | 1k | C22548 | 0603 | SMD |  | $0.063 | $0.126
15 | R18, R19, R20 | 3 | YAGEO | RC0603FR-07100RL | 100 | C105588 | 0603 | SMD |  | $0.021 | $0.126
16 | R21 | 1 | YAGEO | RC0603FR-074R7L | 4.7 | C137705 | 0603 | SMD |  | $0.105 | $0.210
17 | R22 | 1 | YAGEO | RC0603FR-073K3L | 3.3k | C108078 | 0603 | SMD |  | $0.078 | $0.156
18 | LS1, LS2 | 2 | PUI Audio, Inc. | AMM-2742-T-R | AMM-2742-T-R, MEMS Microphones | C3171735 | 0603 | SMD | https://www.mouser.com/ProductDetail/PUI-Audio/AMM-2742-T-R?qs=zhx2xqPtQQyJoGop0O%252BpMA%3D%3D | $2.507 | $10.028 | 7-10 Workdays
19 | IC1 | 1 | Everest-semi(Everest Semiconductor) | ES8388 | ES8388 | C365736 | QFN-28-EP(4x4) | SMD |  | $1.464 | $2.928
20 | D1 | 1 | XINGLIGHT | XL-1608UBC-04 | Blue LED | C965807 | 0603 | SMD |  | $0.215 | $0.430
21 | J1 | 1 | CUI Devices | SJ-3523-SMT-TR | SJ-3523-SMT-TR, 3.5mm Audio Jack |  |  | SMD | https://www.mouser.com/ProductDetail/CUI-Devices/SJ-3523-SMT-TR?qs=WyjlAZoYn51zOHzJ3r4ZRA%3D%3D | $2.113 | $4.226
22 | J3 | 1 | CUI Devices | SJ2-3574A-SMT-TR | SJ2-3574A-SMT-TR, 3.5mm Audio Jack with microphone |  |  | SMD | https://www.mouser.com/ProductDetail/CUI-Devices/SJ2-3574A-SMT-TR?qs=DXv0QSHKF4zeQKpjIMxQnA%3D%3D | $1.916 | $3.832 | 7-10 Workdays
23 | IC2 | 1 | Texas Instruments | TLV9002IDDFR | TLV9002IDDFR, Dual OpAmp | C2862620 | TSOT-23-8 | SMD |  | $0.887 | $1.774 | 7-10 Workdays
 |  |  |  |  |  |  |  |  |  | Component Cost | $27.55

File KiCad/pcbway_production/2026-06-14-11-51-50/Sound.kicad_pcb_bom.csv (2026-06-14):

Designator | Quantity | Value | Footprint | Package | MPN | DNP | Mount_Type | Description
C1, C6 | 2 | 4.7uF | 0603 |  |  |  | smt
C10, C11, C12, C13, C14, C2, C28, C33, C7, C9 | 10 | 0.1uF | 0603 |  |  |  | smt
C15, C16, C17, C18, C19, C20, C29, C3 | 8 | 10uF | 0603 |  |  |  | smt
C21, C22, C23, C24, C27, C4 | 6 | 1.0uF | 0603 |  |  |  | smt
C25, C26 | 2 | 47uF | CAPC1608X100N |  |  |  | smt
C30 | 1 | 1nF | 0603 |  |  |  | smt
C31, C32 | 2 | 22pF | 0603 |  |  |  | smt
C5, C8 | 2 | 500pF | 0603 |  |  |  | smt
D1 | 1 | RED | LED-0603 |  |  |  | smt
IC1 | 1 | ES8388 | QFN45P400X400X80-29N |  |  |  | smt
IC2 | 1 | TLV9062IDDFR | SOT_62IDDFR_TEX-L |  |  |  | smt
J1 | 1 | SJ-3523-SMT-TR | CUI_SJ-3523-SMT-TR |  |  |  | smt
J2 | 1 | CONN_10" | 1X10 |  |  |  | tht
J3 | 1 | SJ2-3574A-SMT-TR | CUI_SJ2-3574A-SMT-TR |  |  |  | smt
J4, J5, J6 | 3 | CONN_02 | 1X02 |  |  |  | tht
JP1 | 1 | Jumper_2_Bridged | Jumper_2_NC_Trace_NoSilk |  |  |  | smt | Jumper, 2-pole, closed/bridged
R1, R12, R15, R17, R5 | 5 | 10k | 0603 |  |  |  | smt
R10, R11, R6, R7, R9 | 5 | 33 | 0603 |  |  |  | smt
R13, R14 | 2 | 2.0k | 0603 |  |  |  | smt
R16 | 1 | 1k | 0603 |  |  |  | smt
R18, R19, R20 | 3 | 100 | 0603 |  |  |  | smt
R2, R3 | 2 | 47k | 0603 |  |  |  | smt
R21 | 1 | 4.7 | 0603 |  |  |  | smt
R22 | 1 | 3.3k | 0603 |  |  |  | smt
R23, R24 | 2 | 1M | 0603 |  |  |  | smt
R29, R30 | 2 | 2.2k | 0603 |  |  |  | smt
R4, R8 | 2 | 20k | 0603 |  |  |  | smt
U1 | 1 | MPRLS0300YG00001B | MPRLS0300YG00001B_HNW |  |  |  | smt

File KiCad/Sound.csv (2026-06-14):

Id | Designator | Footprint | Quantity | Designation | Supplier and ref
1 | C1, C6 | 0603 | 2 | 4.7uF
2 | C2, C7, C9, C10, C11, C12, C13, C14, C28, C33 | 0603 | 10 | 0.1uF
3 | C3, C15, C16, C17, C18, C19, C20, C29 | 0603 | 8 | 10uF
4 | C4, C21, C22, C23, C24, C27 | 0603 | 6 | 1.0uF
5 | C5, C8 | 0603 | 2 | 500pF
6 | C25, C26 | CAPC1608X100N | 2 | 47uF
7 | C30 | 0603 | 1 | 1nF
8 | C31, C32 | 0603 | 2 | 22pF
9 | D1 | LED-0603 | 1 | RED
10 | IC1 | QFN45P400X400X80-29N | 1 | ES8388
11 | IC2 | SOT_62IDDFR_TEX-L | 1 | TLV9062IDDFR
12 | J1 | CUI_SJ-3523-SMT-TR | 1 | SJ-3523-SMT-TR
13 | J2 | 1X10 | 1 | CONN_10";;; 14;J3" | CUI_SJ2-3574A-SMT-TR | 1 | SJ2-3574A-SMT-TR
15 | J4, J5, J6 | 1X02 | 3 | CONN_02
16 | JP1 | Jumper_2_NC_Trace_NoSilk | 1 | Jumper_2_Bridged
17 | R1, R5, R12, R15, R17 | 0603 | 5 | 10k
18 | R2, R3 | 0603 | 2 | 47k
19 | R4, R8 | 0603 | 2 | 20k
20 | R6, R7, R9, R10, R11 | 0603 | 5 | 33
21 | R13, R14 | 0603 | 2 | 2.0k
22 | R16 | 0603 | 1 | 1k
23 | R18, R19, R20 | 0603 | 3 | 100
24 | R21 | 0603 | 1 | 4.7
25 | R22 | 0603 | 1 | 3.3k
26 | R23, R24 | 0603 | 2 | 1M
27 | R29, R30 | 0603 | 2 | 2.2k
28 | U1 | MPRLS0300YG00001B_HNW | 1 | MPRLS0300YG00001B

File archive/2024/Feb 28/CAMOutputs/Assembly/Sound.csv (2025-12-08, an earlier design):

Qty | Value | Device | Package | Parts | Description | DESCRIPTION | DESIGNER | HEIGHT | MANUFACTURER_NAME | MANUFACTURER_PART_NUMBER | MOUSER_PART_NUMBER | MOUSER_PRICE-STOCK | PROD_ID | VALUE | VERSION
1 |  | CONN_06SILK_FEMALE_PTH | 1X06 | J3 | Multi connection point. Often used as Generic Header-pin footprint for 0.1 inch spaced/style header connections |  |  |  |  |  |  |  | CONN-08437
1 |  | CONN_10";1X10" | J2 | Multi connection point. Often used as Generic Header-pin footprint for 0.1 inch spaced/style header connections |  |  |  |  |  |  |  | CONN-11563
1 |  | ES8388ES8388 | ES8388 | J1 | ES8388 PCBArtists Breakout Board
1 | 0.1uF | 0.1UF-0603-25V-(+80/-20%) | 0603 | C3 | 0.1µF ceramic capacitors |  |  |  |  |  |  |  | CAP-00810 | 0.1uF
1 | 1.0uF | 1.0UF-0603-16V-10% | 0603 | C4 | 1µF ceramic capacitors |  |  |  |  |  |  |  | CAP-00868 | 1.0uF
2 | 10k | 10KOHM-0603-1/10W-1% | 0603 | R2, R3 | 10kΩ resistor |  |  |  |  |  |  |  | RES-00824 | 10k
1 | 10uF | 10UF-0603-6.3V-20% | 0603 | C2 | 10.0µF ceramic capacitors |  |  |  |  |  |  |  | CAP-11015 | 10uF
1 | 1k | 1KOHM-0603-1/10W-1% | 0603 | R16 | 1kΩ resistor |  |  |  |  |  |  |  | RES-07856 | 1k
2 | 27pF | 27PF-0603-50V-5% | 0603 | C5, C8 | 27pF ceramic capacitors |  |  |  |  |  |  |  | CAP-09989 | 27pF
2 | 300k | 300KOHM-0603-1/10W-1% | 0603 | R4, R8 | 300kΩ resistor |  |  |  |  |  |  |  | RES-10809 | 300k
2 | 4.7k | 4.7KOHM-0603-1/10W-1% | 0603 | R1, R5 | 4.7kΩ resistor |  |  |  |  |  |  |  | RES-07857 | 4.7k
2 | 4.7uF | 4.7UF0603 | 0603 | C1, C6 | 4.7µF ceramic capacitors |  |  |  |  |  |  |  | CAP-08280 | 4.7uF
2 | AMM-2742-T-R | AMM-2742-T-R | AMM2742TR | LS1, LS2 | Microphones MICROPHONE OMNI -42 DB 2VDC 150uA | Microphones MICROPHONE OMNI -42 DB 2VDC 150uA |  | 0.9mm | PUI Audio | AMM-2742-T-R | 665-AMM-2742-T-R | https://www.mouser.co.uk/ProductDetail/PUI-Audio/AMM-2742-T-R?qs=zhx2xqPtQQyJoGop0O%252BpMA%3D%3D
1 | FRAME-LETTERNO_PACKAGE | FRAME-LETTERNO_PACKAGE | DUMMY | FRAME1 | Schematic Frame - Letter |  | Nobody |  |  |  |  |  |  |  | v01
1 | JUMPER-SMT_2_NC_TRACE_SILK | JUMPER-SMT_2_NC_TRACE_SILK | SMT-JUMPER_2_NC_TRACE_SILK | LED_DISABLE | Normally closed trace jumper
2 | OPA344 | OPA344 | SOT23-5 | U$1, U$2 | Single gate rail-to-rail output op-amp. Inputs extend 300mV past rails. |  |  |  |  |  |  |  | IC-08251 | OPA344
1 | RED | LED-RED0603 | LED-0603 | D1 | Assorted Red LEDs |  |  |  |  |  |  |  | DIO-00819 | RED

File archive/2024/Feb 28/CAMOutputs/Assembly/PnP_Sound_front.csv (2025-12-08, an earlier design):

C1 | 52.75 | 27.25 | 180.00 | 4.7uF | 0603
C2 | 56.90 | 31.40 | 180.00 | 10uF | 0603
C3 | 56.90 | 29.85 | 180.00 | 0.1uF | 0603
C4 | 48.50 | 32.50 | 0.00 | 1.0uF | 0603
C5 | 48.35 | 22.50 | 180.00 | 27pF | 0603
C6 | 52.50 | 20.75 | 180.00 | 4.7uF | 0603
C8 | 48.35 | 16.00 | 180.00 | 27pF | 0603
D1 | 10.75 | 7.25 | 180.00 | RED | LED-0603
LED_DISABLE | 10.75 | 5.00 | 90.00 | JUMPER-SMT_2_NC_TRACE_SILK | SMT-JUMPER_2_NC_TRACE_SILK
LS1 | 57.25 | 26.25 | 0.00 | AMM-2742-T-R | AMM2742TR
LS2 | 57.25 | 19.75 | 0.00 | AMM-2742-T-R | AMM2742TR
R1 | 52.75 | 25.50 | 180.00 | 4.7k | 0603
R16 | 10.75 | 10.25 | 90.00 | 1k | 0603
R2 | 48.50 | 29.50 | 0.00 | 10k | 0603
R3 | 48.50 | 31.00 | 180.00 | 10k | 0603
R4 | 48.35 | 24.05 | 180.00 | 300k | 0603
R5 | 52.50 | 19.00 | 180.00 | 4.7k | 0603
R8 | 48.35 | 17.50 | 180.00 | 300k | 0603
U$1 | 48.50 | 26.50 | 270.00 | OPA344 | SOT23-5
U$2 | 48.50 | 19.95 | 270.00 | OPA344 | SOT23-5

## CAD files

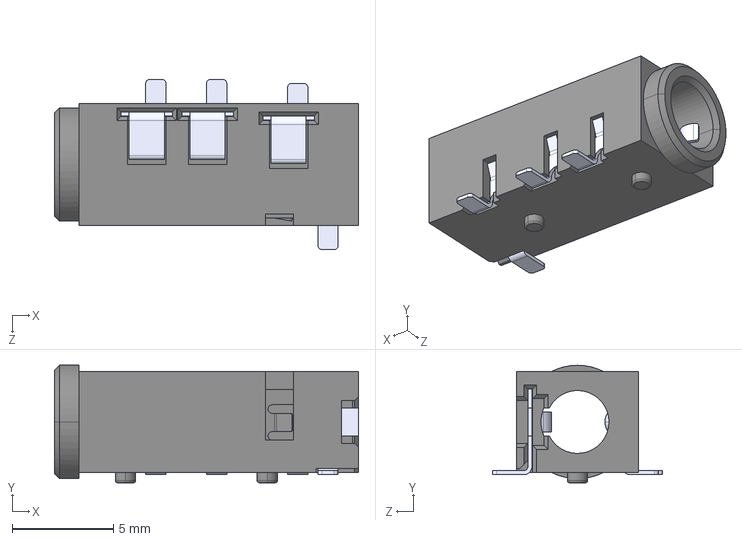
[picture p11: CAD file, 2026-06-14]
KiCad/Sound.3d/SJ2-3574A-SMT-TR--3DModel-STEP-56544.STEP
15.0 x 5.80 x 8.40 mm

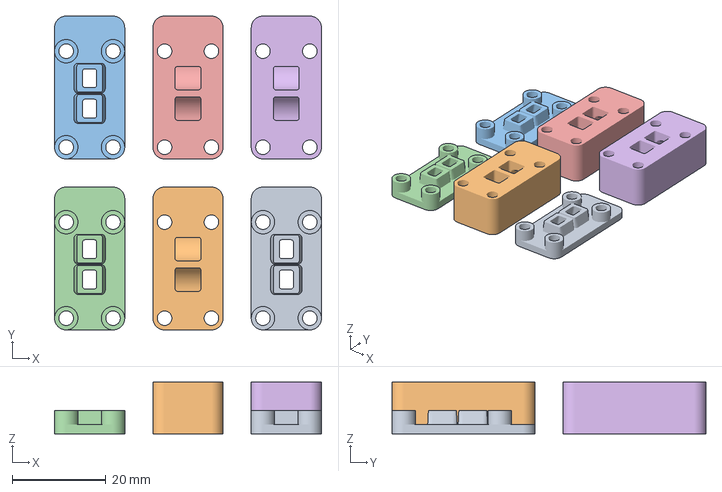
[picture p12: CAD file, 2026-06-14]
Models/MicrophoneHousing.3mf
57.0 x 67.0 x 11.0 mm
MicrophoneBottom.stl x 3
MicrophoneTop.stl x 3

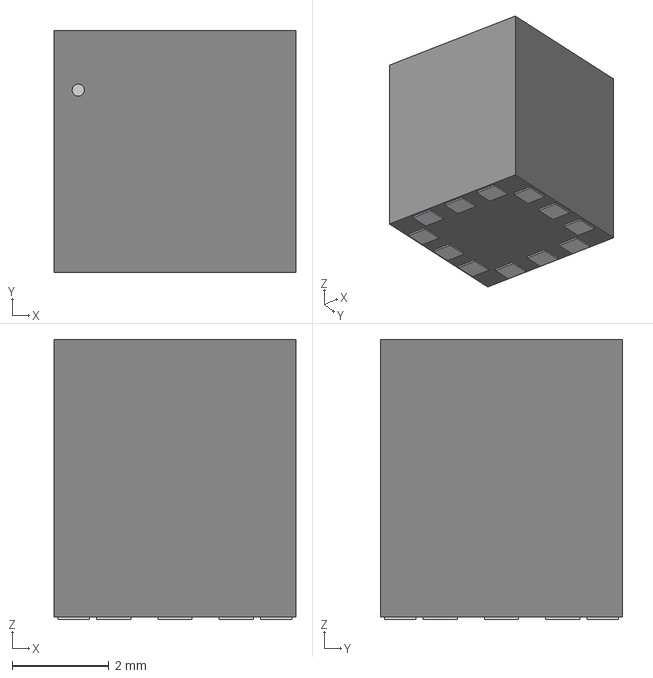
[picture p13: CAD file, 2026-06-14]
KiCad/Sound.3d/MPRLS0300YG00001B_HNW.step
5.00 x 5.00 x 5.79 mm

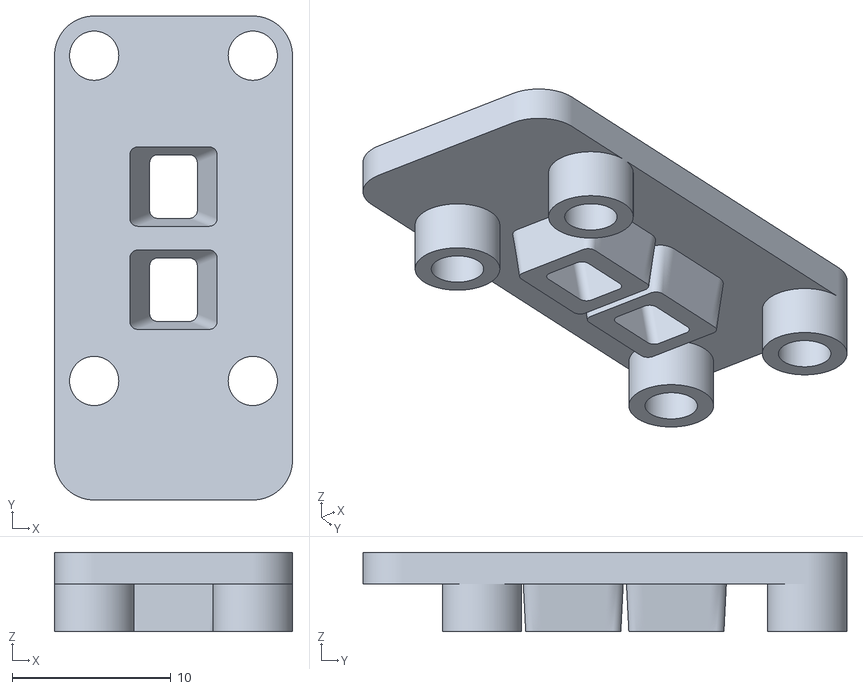
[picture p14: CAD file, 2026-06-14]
Models/MicrophoneBottom.stl
15.0 x 30.5 x 5.00

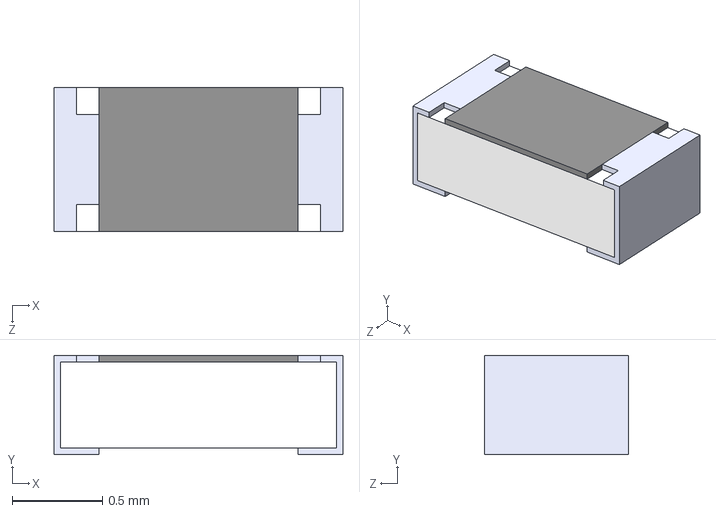
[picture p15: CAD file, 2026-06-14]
KiCad/Sound.3d/RC0603FR-07220RL.STEP
1.60 x 0.55 x 0.8 mm

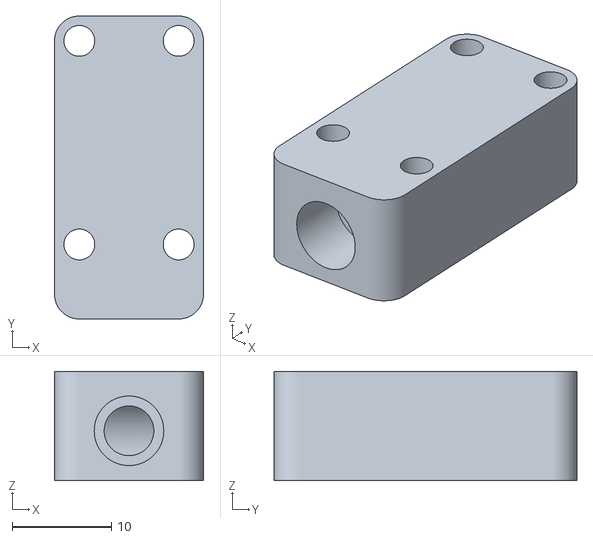
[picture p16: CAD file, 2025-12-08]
Models/MicrophoneTop.stl
15.0 x 30.5 x 11.0

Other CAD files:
KiCad/Sound.3d/MPRLS0300YG00001B_HNW.stl

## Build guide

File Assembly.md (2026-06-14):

# Assembly of Stethoscope & Blood Pressure MediBrick

## Required Parts

- Fully assembled Stethoscope PCB
- Microcontroller board:
  - Adafruit Feather ESP32-S3, or
  - SparkFun Thing Plus C
- Honeywell MPRLS0300YG pressure sensor
- OLED display
- Pushbutton
- Battery
- AWG 22 or AWG 24 silicone wire
- Stainless steel tubing, 7 mm OD, 5 mm ID
- Stethoscope chest piece and tubing
- Inflatable arm cuff
- Silicone tubing
- Luer lock adapters
- Miscellaneous hardware:
  - M3 screws, 20 mm, and nuts for PCB mounting
  - M3 & M2.5 screws for microcontroller / enclosure mounting
  - Plastic washers

## 3D Printed Parts

For the design models, refer to the README.

- MediBrick Outer Casing
  - Outer casing top part
  - Outer casing bottom part
- Microphone Housing
  - Microphone housing has not been updated yet for new 10mm microphones.
- Side plate

## Tubing and Adapter Notes

- Suggested stethoscope rubber tube: **5 mm ID**, using a barb with **8 mm OD**
- Suggested pressure cuff tube: **4 mm ID**, using a barb with **7 mm OD**
- Rubber tubing from Honeywell pressure sensor to arm cuff: **2 mm ID, 4 mm OD**
- Luer Lock **3/32** barbed adapter for rubber tubing from pressure sensor
- Luer Lock **5/32** barbed adapter for pressure cuff tube

## Required Tools

- Soldering iron
- Hot-air rework station
- Solder
- Flux
- Tweezers
- Isopropyl alcohol
- Small screwdrivers
- Wire cutters / wire strippers
- Continuity tester or multimeter

---

# Assembly Procedure

## 1. Collect and inspect all parts

Verify that all electrical, mechanical, and tubing components are present before beginning assembly. Inspect the PCB, 3D-printed parts, and microcontroller board for visible damage or manufacturing defects.

## 2. Solder the pressure sensor to the PCB

Use a hot-air rework station to solder the **Honeywell MPRLS0300YG** pressure sensor to the board. For ease of soldering, also heat the assembled board with a [miniture hot plate from Adafruit](https://www.adafruit.com/product/4948) or [from AliExpress](https://www.aliexpress.us/item/3256806194378309.html)

1. Locate the pressure sensor footprint on the PCB. The solder pads form a square pattern.
2. Identify the orientation marker on the PCB footprint. One corner of the footprint has a dot.
3. Apply flux to the pressure sensor pads on the PCB. A generous amount of flux is acceptable.
4. Inspect the underside of the pressure sensor and locate its orientation dot.
5. Place the pressure sensor onto the PCB footprint, aligning the dot on the sensor with the dot on the PCB.
6. Set the hotplate to approximately **200 °C**.
7. Set the hot-air station to approximately **350 °C**.
8. Let the temperature of the hotplate increase.
9. Using gentle airflow, heat the pressure sensor evenly from above until the solder reflows and the sensor settles into place.
10. Do **not** push the sensor while the solder is molten.
11. Remove the hot air and allow the board to cool before touching or moving the sensor.
12. Clean the flux residue using isopropyl alcohol.

## 3. Attach wires to the PCB and microcontroller

Attach color-coded wires to the PCB I/O pads. A suggested color convention is:

- **Red** for power
- **Black** or **green** for ground
- **Blue** or **white** for digital input/output
- **Yellow** for analog wires

Wires may be inserted into the pad holes or soldered perpendicularly onto the pads. Route all wires carefully and avoid excessive strain on the solder joints.

> The PCB is vulnerable to shorts, so inspect closely for solder bridges or unintended conductive paths before power-up.

---

# Electrical Connections

## Main PCB Connections

Suggested connections for the SparkFun Thing Plus C (USB-C) and Adafruit Feather ESP32-S3 are given below.

| PAD | Function | Thing Plus | Feather |
|---|---|---|---|
| **GND** | Ground | GND | GND |
| **3.3V** | Power | 3V3 | 3V3 |
| **SDA** | SDA / CDATA | SDA / GPIO21 | SDA / GPIO3 |
| **SCL** | SCL / CCLK | SCL / GPIO22 | SCL / GPIO4 |
| **DOUT** | Data Out | POCI / GPIO19 | MISO / GPIO37 |
| **LRCLK** | WS / Word Clock | A5 / GPIO35 | A5 / GPIO8 / ADC1-CH7 |
| **DIN** | Data In / DSDIN | PICO / GPIO23 | MOSI / GPIO35 |
| **SLCK** | Bit Clock | SCK / GPIO18 | SCK / GPIO36 |
| **MCLK** | Master Clock | LED / GPIO13 | A4 / GPIO14 / ADC2-CH3 |
| **3.3V** | Power | 3V3 | 3V3 |

Required connections are shown in **bold**.

## Button

| PAD | Function | Thing Plus | Feather |
|---|---|---|---|
| **3.3V** | Power | 3V3 | 3V3 |
| **Button** | Button signal | 9 or A0 | 12 |

## OLED Display

| PAD | Function | Thing Plus | Feather |
|---|---|---|---|
| **VCC** | Power |  | 3V3 |
| **GND** | Ground |  | GND |
| **SDA** | I2C Data |  | 3 |
| **SCL** | I2C Clock |  | 4 |

## Pressure Sensor Control Lines

The MPRLS0300YG also requires two signal wires to the ESP32-S3 board.

| PAD | Function | Thing Plus | Feather |
|---|---|---|---|
| **EOC** | End of Conversion |  | D10 |
| **RST** | Reset |  | D11 |

---

# Mechanical Assembly

## 4. Mount the PCB into the enclosure

Place the custom PCB into the **bottom portion of the outer casing** and secure it using the appropriate M3 screws and nuts. Make sure the board is seated properly and that no wires are trapped beneath it.

## 5. Mount the microcontroller board

Position the microcontroller board in its designated location within the enclosure and secure it with the appropriate hardware. Route the wires neatly so they do not place excessive strain on the solder joints.

## 6. Assemble and install the microphone housing

Attach the microphone housing top and bottom parts and secure them with the required screws. Ensure that the housing is aligned correctly and that the PCB-mounted microphones remain unobstructed.

## 7. Insert the stainless steel tube into the microphone housing

Place the stainless steel tube into the microphone housing so that it forms the acoustic path between the stethoscope tubing and the microphone assembly. Verify that the tube is seated securely.

## 8. Connect the stethoscope tubing

Attach the stethoscope tubing to the microphone housing interface. Ensure a secure fit, since poor acoustic coupling may reduce heartbeat audibility.

## 9. Connect the pressure tubing

Attach the silicone tubing and luer lock adapters to connect the pressure cuff path to the Honeywell pressure sensor.

- Use the **2 mm ID / 4 mm OD** tubing segment for the pressure sensor connection
- Use the correct luer lock adapters for the pressure sensor and cuff tubing
- Verify that all pressure connections are secure and free from leaks

## 10. Install the display, button, and battery

Mount the OLED display, pushbutton, and battery according to the final enclosure layout. Confirm that:

- the display is visible through the enclosure opening
- the pushbutton is accessible
- the battery is seated securely

## 11. Close the enclosure

Install the **top portion of the outer casing** and secure it to the bottom portion. During closure, make sure no wires or tubing are pinched and that all components remain properly seated.

---

# Final Inspection and Power-Up

## 12. Perform final inspection

Before applying power:

- inspect the PCB for shorts or solder bridges
- verify all wiring against the pin tables above
- confirm tubing paths are secure
- check mounting hardware
- ensure the enclosure closes cleanly without pinching wires or tubing

## 13. Power on and verify basic functionality

Apply power to the device and confirm successful startup. Verify:

- OLED operation
- pressure sensing
- audio output
- button response

After basic functionality is confirmed, the device is ready for formal verification testing.

---

# Pinout References

- [SparkFun Thing Plus C Pinout](https://cdn.sparkfun.com/assets/3/9/5/f/e/SparkFun_Thing_Plus_ESP32_WROOM_C_graphical_datasheet2.pdf)
- [Adafruit ESP32-S3 Pinout](https://learn.adafruit.com/adafruit-esp32-s3-feather/pinouts)

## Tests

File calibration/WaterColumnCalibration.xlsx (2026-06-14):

Default Settings from Datasheet
Zero | 419430.4
Count | 3774873.6 |  |  |  | 3355443.2
Height | Default |  | 300 | 5.80104 | 1.728844643e-06 | Expected Value
 |  |  |  |  | 0.03549893488 | Error | 120 | 124.2598722
Zero | 417000 |  |  |  | delta Counts
Count | 1450630 | mmH2O | mmHg | PSI | 1033630
Height | 50.8125 | 1290.6375 | 94.93400289 | 1.835717598 | 1.77599102e-06
Zero | 413500 |  |  |  | delta Counts
Count | 1488000 | mmH2O | mmHg | PSI | 1074500
Height | 53 | 1346.2 | 99.02095258 | 1.914746031 | 1.78198793e-06
Zero | 414800 |  |  |  | delta Counts
Count | 1176500 | mmH2O | mmHg | PSI | 761700
Height | 38.125 | 968.375 | 71.22969466 | 1.377352687 | 1.808261372e-06
Zero | 416100 |  |  |  | delta Counts
Count | 1730600 | mmH2O | mmHg | PSI | 1314500
Height | 65 | 1651 | 121.4407909 | 2.348273434 | 1.78643852e-06
Zero | 412800 |  |  |  | delta Counts
Count | 1709700 | mmH2O | mmHg | PSI | 1296900
Height | 64.875 | 1647.825 | 121.2072509 | 2.343757524 | 1.807199879e-06
Zero | 415200 |  |  |  | delta Counts
Count | 1719000 | mmH2O | mmHg | PSI | 1303800
Height | 64.125 | 1628.775 | 119.806011 | 2.316662061 | 1.776853859e-06
 |  |  |  |  |  | Average Zero
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

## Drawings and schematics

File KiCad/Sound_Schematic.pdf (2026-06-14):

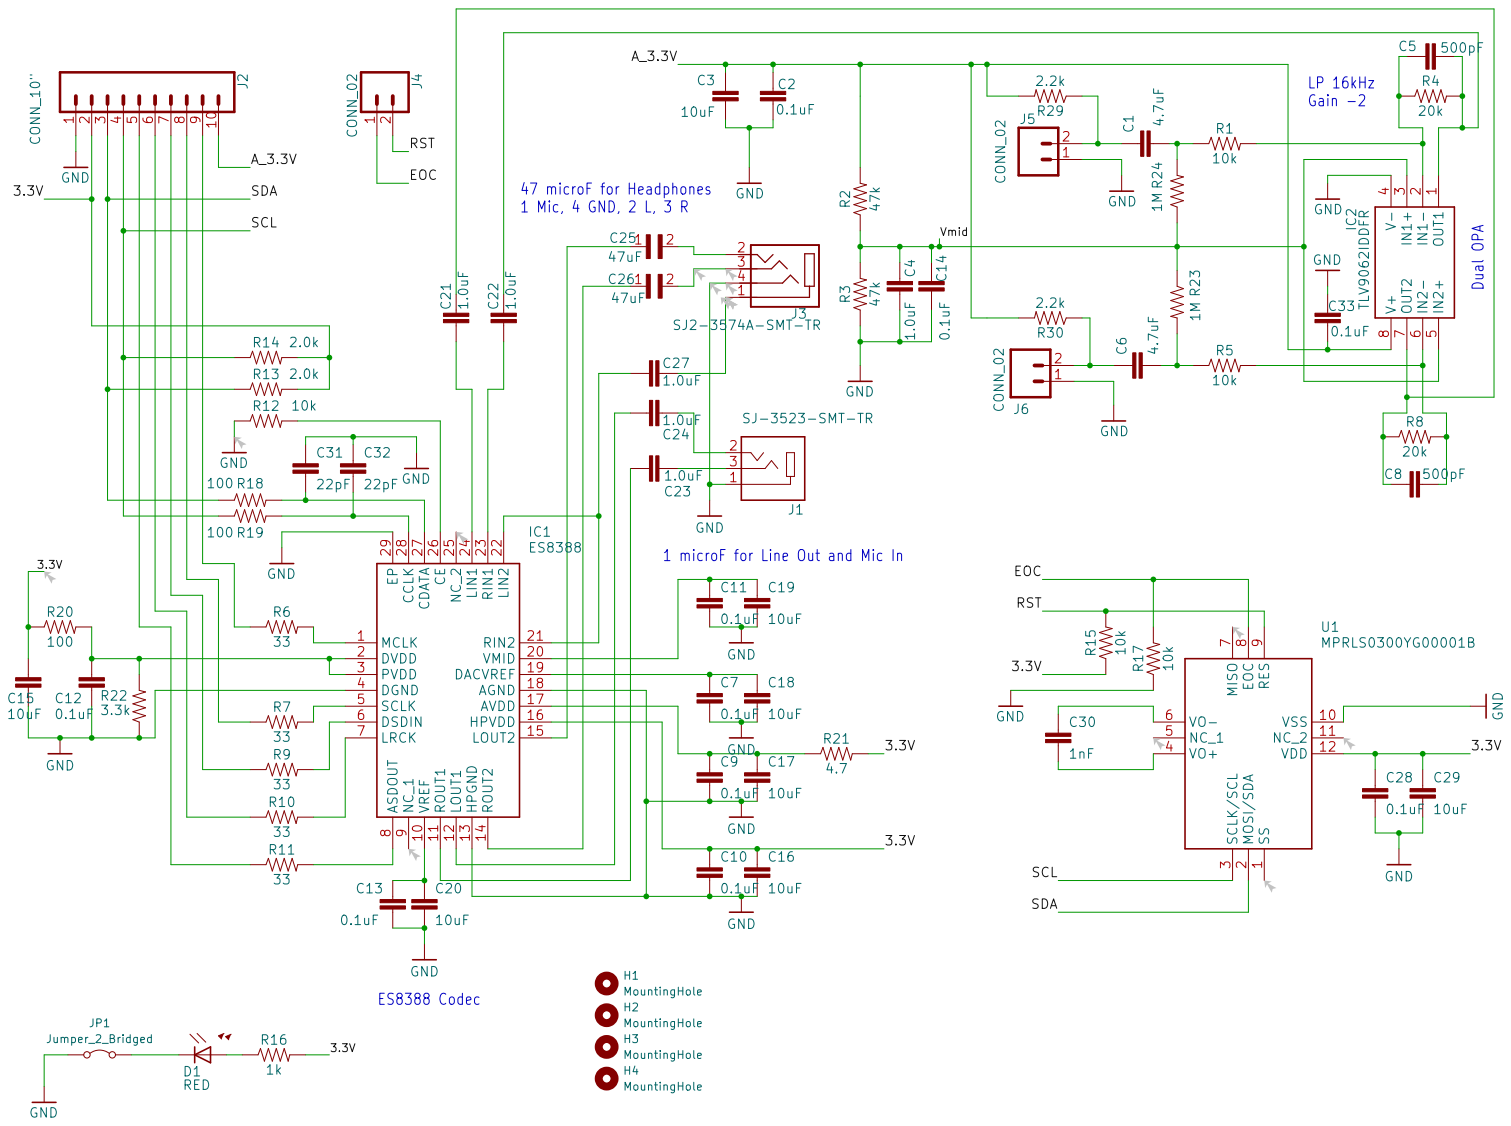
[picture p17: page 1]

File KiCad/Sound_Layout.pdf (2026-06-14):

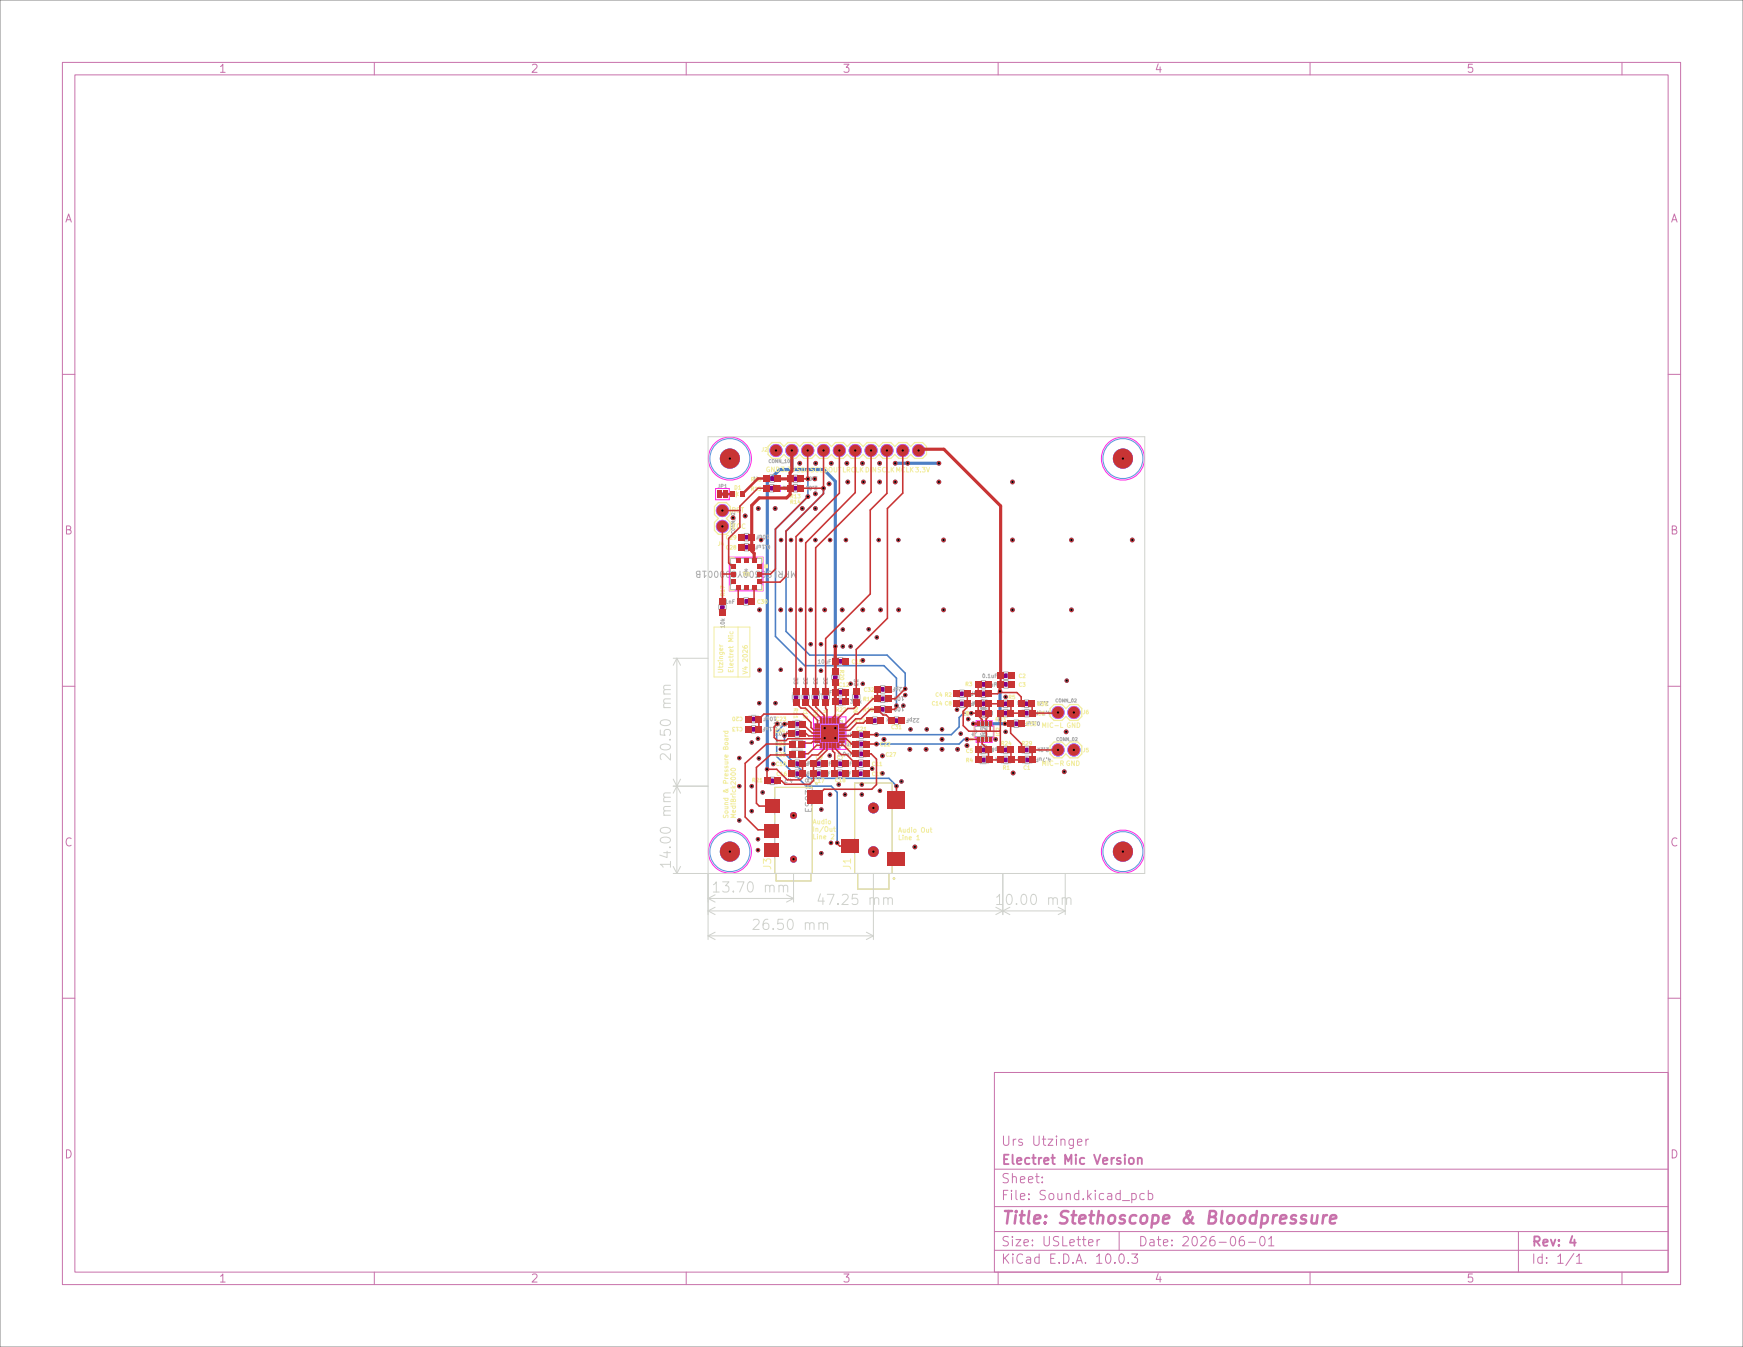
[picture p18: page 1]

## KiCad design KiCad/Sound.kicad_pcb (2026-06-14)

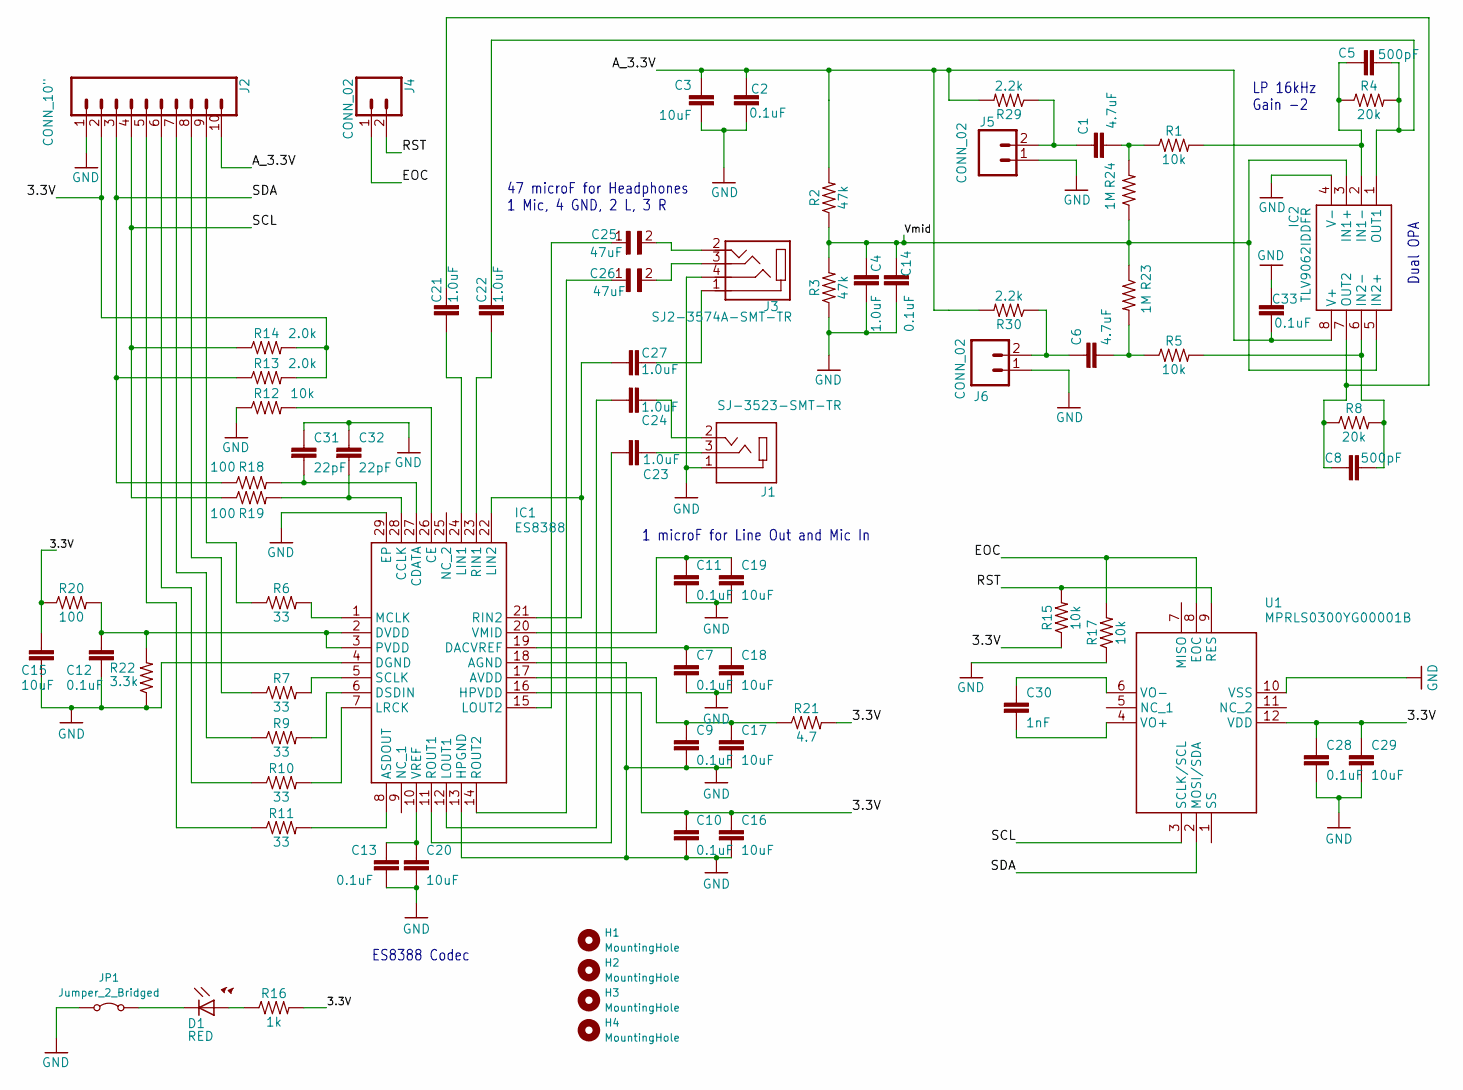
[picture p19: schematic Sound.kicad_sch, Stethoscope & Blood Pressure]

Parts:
C1, C6: 4.7uF; 0603
C2, C7, C9, C10, C11, C12, C13, C14, C28, C33: 0.1uF; 0603
C3, C15, C16, C17, C18, C19, C20, C29: 10uF; 0603
C4, C21, C22, C23, C24, C27: 1.0uF; 0603
C5, C8: 500pF; 0603
C25, C26: 47uF; CAPC1608X100N
C30: 1nF; 0603
C31, C32: 22pF; 0603
D1: RED; LED-0603
H1, H2, H3, H4: MountingHole; MountingHole_3.2mm_M3
IC1: ES8388; QFN45P400X400X80-29N
IC2: TLV9062IDDFR; SOT_62IDDFR_TEX-L
J1: SJ-3523-SMT-TR; CUI_SJ-3523-SMT-TR
J2: CONN_10"; 1X10
J3: SJ2-3574A-SMT-TR; CUI_SJ2-3574A-SMT-TR
J4, J5, J6: CONN_02; 1X02
JP1: Jumper_2_Bridged; Jumper_2_NC_Trace_NoSilk
R1, R5, R12, R15, R17: 10k; 0603
R2, R3: 47k; 0603
R4, R8: 20k; 0603
R6, R7, R9, R10, R11: 33; 0603
R13, R14: 2.0k; 0603
R16: 1k; 0603
R18, R19, R20: 100; 0603
R21: 4.7; 0603
R22: 3.3k; 0603
R23, R24: 1M; 0603
R29, R30: 2.2k; 0603
U1: MPRLS0300YG00001B; MPRLS0300YG00001B_HNW

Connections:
/3.3V: C10.1, C15.1, C16.1, C28.1, C29.1, IC1.16 (HPVDD), J2.2, R13.2, R14.2, R15.1, R16.2, R20.1, R21.2, U1.12 (VDD)
/A_3.3V: C2.1, C3.1, C33.2, IC2.8 (V+), J2.10, R2.2, R29.2, R30.2
/EOC: J4.1, R17.2, U1.8 (EOC)
/RST: J4.2, R15.2, U1.9 (RES)
/SCL: J2.4, R14.1, R19.1, U1.3 (SCLK/SCL)
/SDA: J2.3, R13.1, R18.1, U1.2 (MOSI/SDA)
/Vmid: C4.1, C14.1, IC2.3 (IN1+), IC2.5 (IN2+), R2.1, R3.2, R23.1, R24.1
GND: C2.2, C3.2, C4.2, C7.2, C9.2, C10.2, C11.2, C12.2, C13.2, C14.2, C15.2, C16.2, C17.2, C18.2, C19.2, C20.2, C28.2, C29.2, C31.1, C32.1, C33.1, IC1.4 (DGND), IC1.13 (HPGND), IC1.18 (AGND), IC1.29 (EP), IC2.4 (V-), J1.1, J2.1, J3.4, J5.1, J6.1, JP1.1 (A), R3.1, R12.1, R17.1, R22.1, U1.10 (VSS)
unnamed: C1.1, J5.2, R29.1
unnamed: C1.2, R1.1, R24.2
unnamed: C6.1, J6.2, R30.1
unnamed: C6.2, R5.1, R23.2
unnamed: C23.1, J1.3
unnamed: C24.1, J1.2
unnamed: C25.2, J3.2
unnamed: C26.2, J3.3
unnamed: C27.2, J3.1
unnamed: D1.A, R16.1
unnamed: IC1.8 (ASDOUT), R11.2
unnamed: C9.1, C17.1, IC1.17 (AVDD), R21.1
unnamed: C32.2, IC1.28 (CCLK), R19.2
unnamed: C31.2, IC1.27 (CDATA), R18.2
unnamed: IC1.26 (CE), R12.2
unnamed: C7.1, C18.1, IC1.19 (DACVREF)
unnamed: IC1.6 (DSDIN), R9.2
unnamed: C12.1, IC1.2 (DVDD), IC1.3 (PVDD), R20.2, R22.2
unnamed: C21.1, IC1.24 (LIN1)
unnamed: C27.1, IC1.21 (RIN2), IC1.22 (LIN2)
unnamed: C24.2, IC1.12 (LOUT1)
unnamed: C25.1, IC1.15 (LOUT2)
unnamed: IC1.7 (LRCK), R10.2
unnamed: IC1.1 (MCLK), R6.2
unnamed: C22.1, IC1.23 (RIN1)
unnamed: C23.2, IC1.11 (ROUT1)
unnamed: C26.1, IC1.14 (ROUT2)
unnamed: IC1.5 (SCLK), R7.2
unnamed: C11.1, C19.1, IC1.20 (VMID)
unnamed: C13.1, C20.1, IC1.10 (VREF)
unnamed: C5.1, IC2.2 (IN1-), R1.2, R4.1
unnamed: C8.2, IC2.6 (IN2-), R5.2, R8.2
unnamed: C5.2, C22.2, IC2.1 (OUT1), R4.2
unnamed: C8.1, C21.2, IC2.7 (OUT2), R8.1
unnamed: J2.5, R11.1
unnamed: J2.6, R10.1
unnamed: J2.7, R9.1
unnamed: J2.8, R7.1
unnamed: J2.9, R6.1
unnamed: D1.C, JP1.2 (B)
unnamed: C30.2, U1.4 (VO+)
unnamed: C30.1, U1.6 (VO-)

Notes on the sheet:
ES8388 Codec
1 microF for Line Out and Mic In
LP 16kHz Gain -2
Dual OPA
47 microF for Headphones 1 Mic, 4 GND, 2 L, 3 R

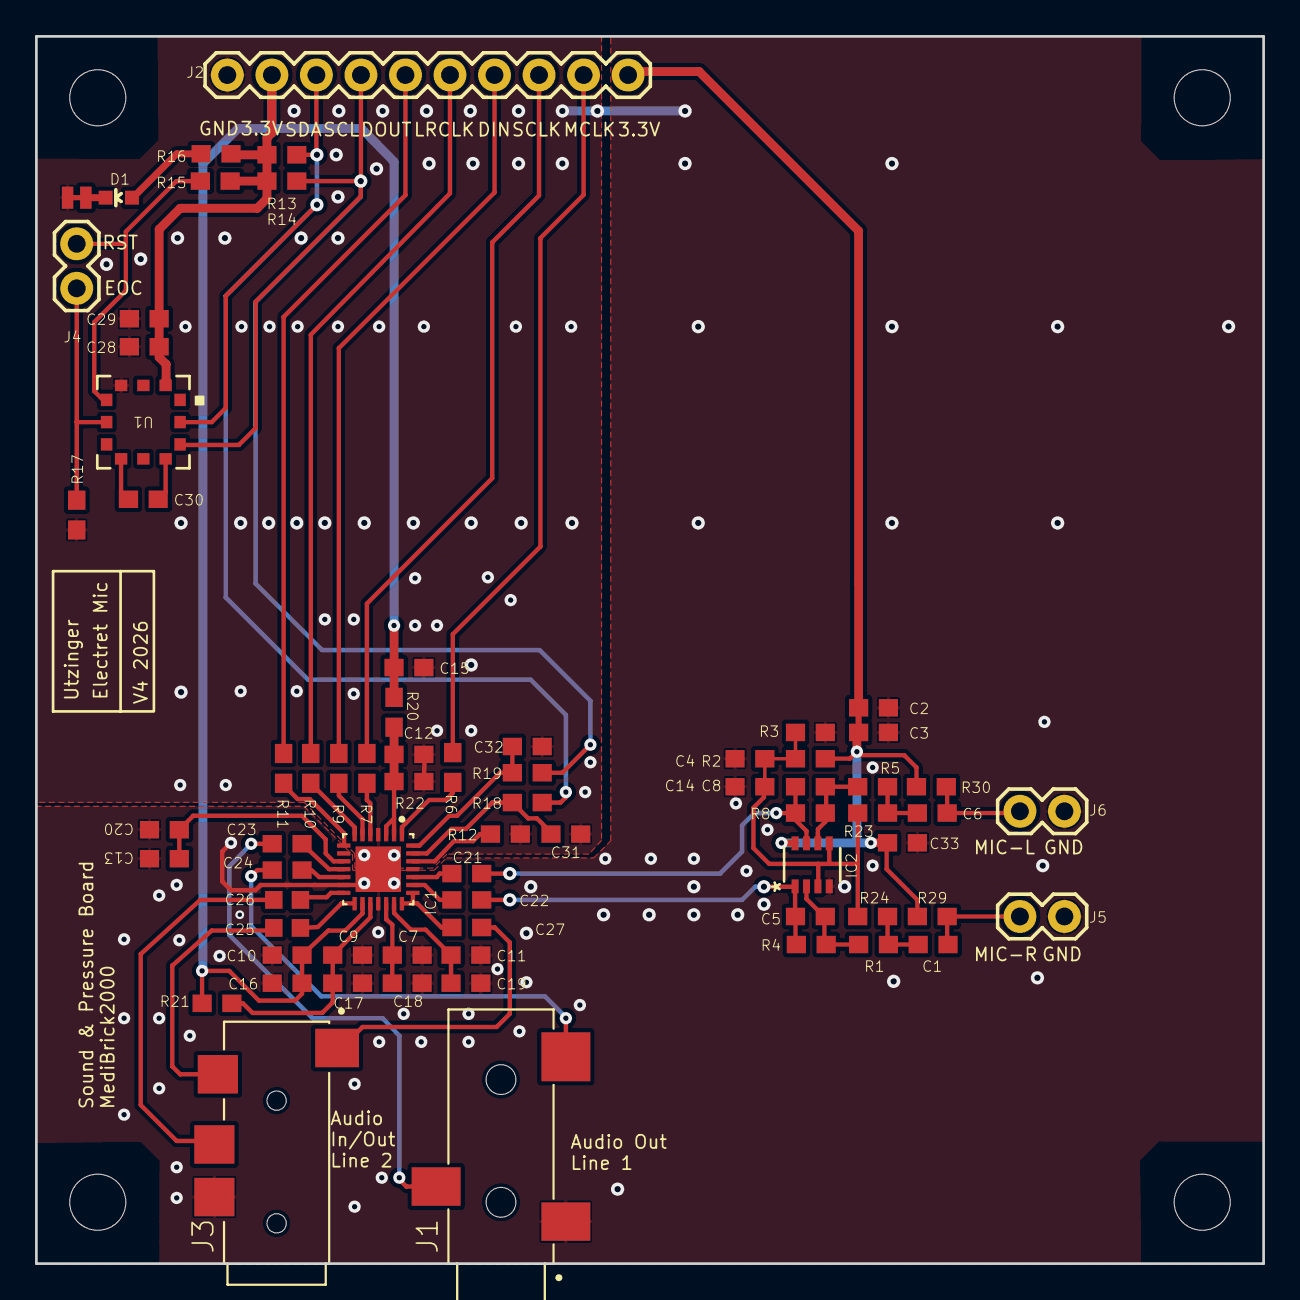
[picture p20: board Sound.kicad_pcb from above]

Board: 2 copper layers, 70.0 x 70.0 mm, 74 parts (0 on the bottom side), 50 nets.

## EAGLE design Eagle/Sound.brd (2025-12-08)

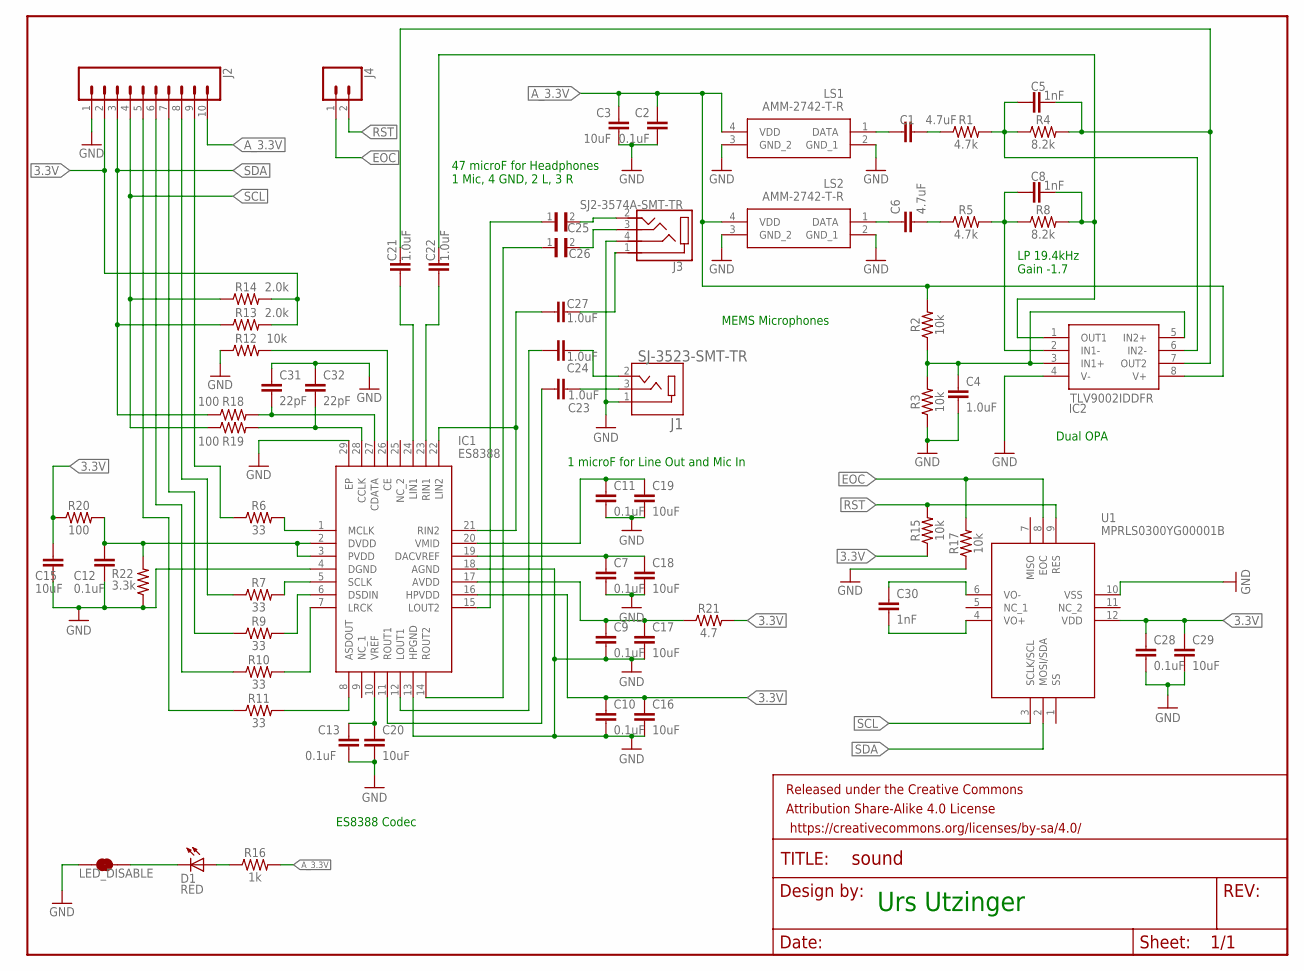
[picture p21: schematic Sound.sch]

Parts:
C1, C6: 4.7uF; 0603
C2, C7, C9, C10, C11, C12, C13, C28: 0.1uF; 0603
C3, C15, C16, C17, C18, C19, C20, C29: 10uF; 0603
C4, C21, C22, C23, C24, C27: 1.0uF; 0603
C5, C8, C30: 1nF; 0603
C25, C26: GRM188R60J476ME15D; CAPC1608X100N
C31, C32: 22pF; 0603
D1: RED; LED-0603
FRAME1: FRAME-LETTERNO_PACKAGE; DUMMY
IC1: ES8388; QFN45P400X400X90-29N
IC2: TLV9002IDDFR; SOT65P280X110-8N
J1: SJ-3523-SMT-TR; CUI_SJ-3523-SMT-TR
J2: CONN_10"; 1X10
J3: SJ2-3574A-SMT-TR; CUI_SJ2-3574A-SMT-TR
J4: CONN_02; 1X02
LED_DISABLE: JUMPER-SMT_2_NC_TRACE_SILK; SMT-JUMPER_2_NC_TRACE_SILK
LS1, LS2: AMM-2742-T-R; AMM2742TR
R1, R5: 4.7k; 0603
R2, R3, R12, R15, R17: 10k; 0603
R4, R8: 8.2k; 0603
R6, R7, R9, R10, R11: 33; 0603
R13, R14: 2.0k; 0603
R16: 1k; 0603
R18, R19, R20: 100; 0603
R21: 4.7; 0603
R22: 3.3k; 0603
U1: MPRLS0300YG00001B

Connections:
3.3V: C10.1, C15.1, C16.1, C28.1, C29.1, IC1.16 (HPVDD), J2.2, R13.2, R14.2, R15.1, R20.1, R21.2, U1.12 (VDD)
A_3.3V: C2.1, C3.1, IC2.8 (V+), J2.10, LS1.4 (VDD), LS2.4 (VDD), R2.2, R16.2
DIN: J2.7, R9.1
DOUT: J2.5, R11.1
EOC: J4.1, R17.2, U1.8 (EOC)
GND: C2.2, C3.2, C4.2, C7.2, C9.2, C10.2, C11.2, C12.2, C13.2, C15.2, C16.2, C17.2, C18.2, C19.2, C20.2, C28.2, C29.2, C31.1, C32.1, IC1.4 (DGND), IC1.13 (HPGND), IC1.18 (AGND), IC1.29 (EP), IC2.4 (V-), J1.1, J2.1, J3.4, LED_DISABLE.1, LS1.2 (GND_1), LS1.3 (GND_2), LS2.2 (GND_1), LS2.3 (GND_2), R3.1, R12.1, R17.1, R22.1, U1.10 (VSS)
LRCLK: J2.6, R10.1
MCLK: J2.9, R6.1
unnamed: IC1.26 (CE), R12.2
unnamed: C8.2, C22.2, IC2.1 (OUT1), R8.2
unnamed: C22.1, IC1.23 (RIN1)
unnamed: C21.1, IC1.24 (LIN1)
unnamed: C31.2, IC1.27 (CDATA), R18.2
unnamed: C32.2, IC1.28 (CCLK), R19.2
unnamed: C11.1, C19.1, IC1.20 (VMID)
unnamed: C30.1, U1.6 (VO-)
unnamed: C5.2, C21.2, IC2.7 (OUT2), R4.2
unnamed: C30.2, U1.4 (VO+)
unnamed: C1.1, LS1.1 (DATA)
unnamed: C9.1, C17.1, IC1.17 (AVDD), R21.1
unnamed: C1.2, R1.1
unnamed: C5.1, IC2.6 (IN2-), R1.2, R4.1
unnamed: C4.1, IC2.3 (IN1+), IC2.5 (IN2+), R2.1, R3.2
unnamed: C12.1, IC1.2 (DVDD), IC1.3 (PVDD), R20.2, R22.2
unnamed: C6.1, LS2.1 (DATA)
unnamed: C6.2, R5.1
unnamed: C8.1, IC2.2 (IN1-), R5.2, R8.1
unnamed: IC1.8 (ASDOUT), R11.2
unnamed: IC1.7 (LRCK), R10.2
unnamed: C13.1, C20.1, IC1.10 (VREF)
unnamed: IC1.6 (DSDIN), R9.2
unnamed: IC1.5 (SCLK), R7.2
unnamed: D1.A, R16.1
unnamed: IC1.1 (MCLK), R6.2
unnamed: D1.C, LED_DISABLE.2
unnamed: C23.2, IC1.11 (ROUT1)
unnamed: C24.1, J1.2
unnamed: C7.1, C18.1, IC1.19 (DACVREF)
unnamed: C24.2, IC1.12 (LOUT1)
unnamed: C25.2, J3.2
unnamed: C23.1, J1.3
unnamed: C26.2, J3.3
unnamed: C27.2, J3.1
unnamed: C27.1, IC1.21 (RIN2), IC1.22 (LIN2)
unnamed: C26.1, IC1.14 (ROUT2)
unnamed: C25.1, IC1.15 (LOUT2)
RST: J4.2, R15.2, U1.9 (RES)
SCL: J2.4, R14.1, R19.1, U1.3 (SCLK/SCL)
SCLK: J2.8, R7.1
SDA: J2.3, R13.1, R18.1, U1.2 (MOSI/SDA)

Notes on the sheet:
MEMS Microphones
Dual OPA
47 microF for Headphones 1 Mic, 4 GND, 2 L, 3 R
1 microF for Line Out and Mic In
Urs Utzinger
ES8388 Codec
LP 19.4kHz Gain -1.7

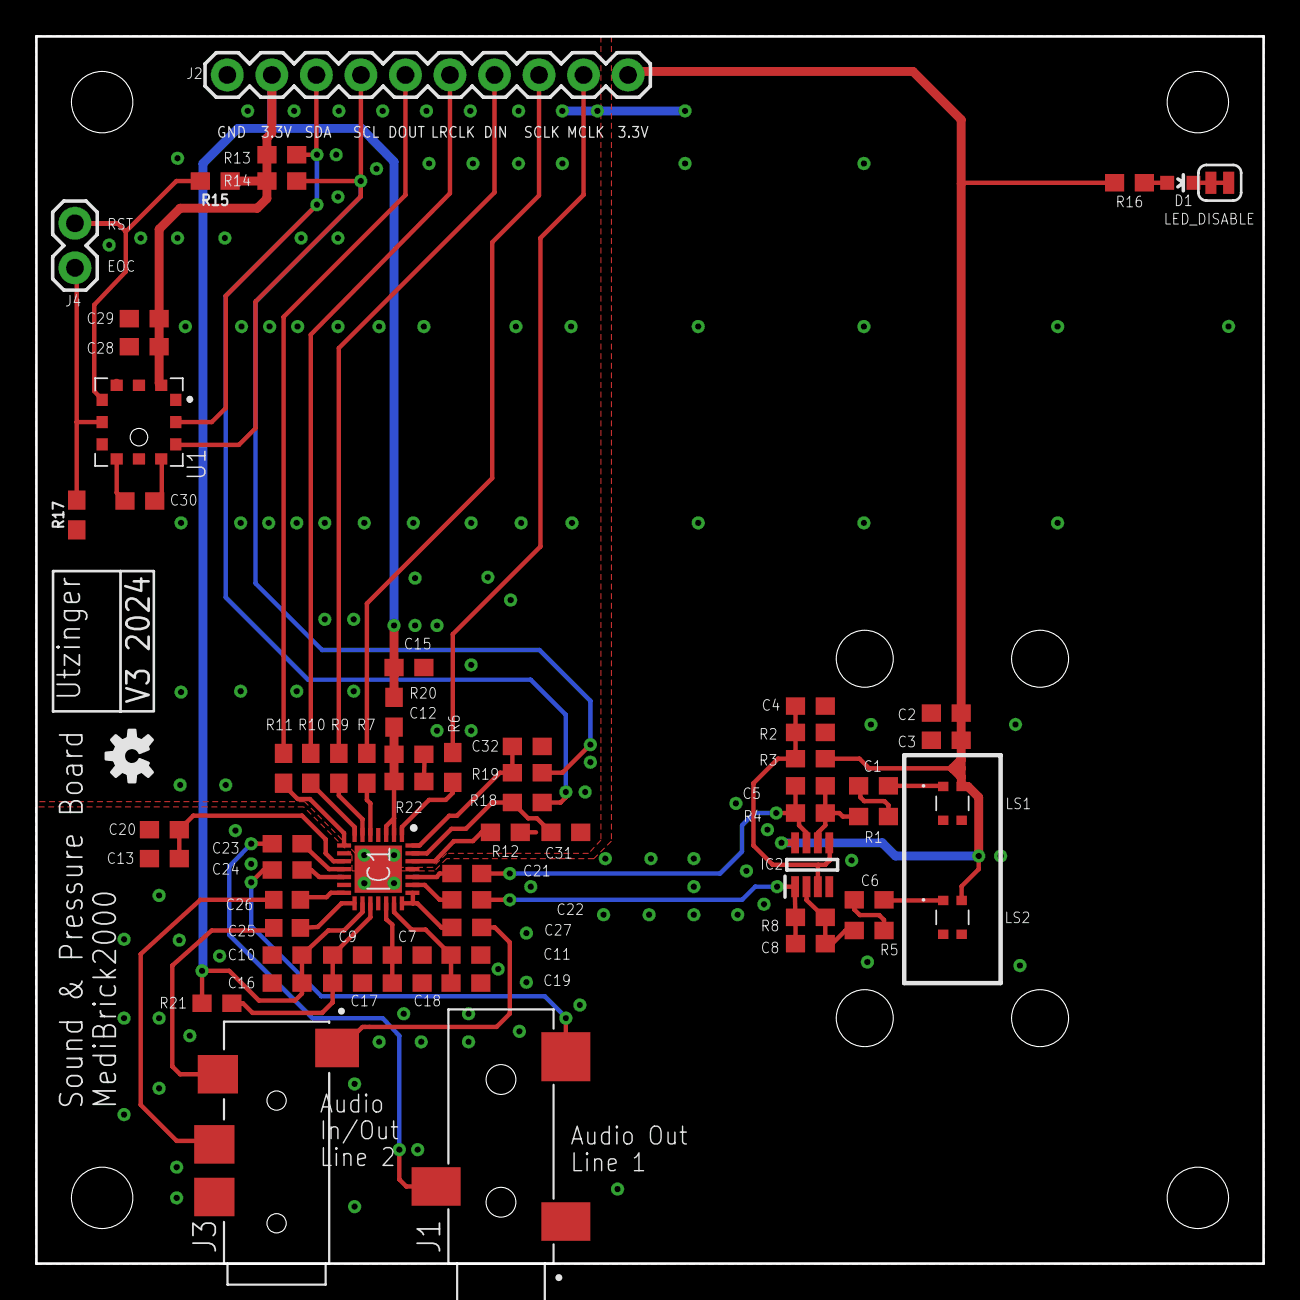
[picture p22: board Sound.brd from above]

Board: 2 copper layers, 70.0 x 70.0 mm, 66 parts (0 on the bottom side), 50 nets.

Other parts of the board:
U$3: OSHW-LOGO-S

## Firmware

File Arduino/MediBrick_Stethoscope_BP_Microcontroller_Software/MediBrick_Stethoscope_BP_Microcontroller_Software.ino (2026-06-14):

/*
  MediBrick Stethoscope + Blood Pressure
  ESP32-S3 Feather

  Runtime Serial Commands:
    p = Pressure only
    s = Stethoscope only
    b = Both (pressure on OLED + audio active)
    ? = Help
    < = output volume down
    > = output volume up
    , = input volume down
    . = input volume up
    + = software gain up
    - = software gain down
    L/l = low-pass cutoff up/down
    H/h = high-pass cutoff up/down
    G/g = high-pass ON/OFF
    K/k = low-pass ON/OFF
    N/n = noise cancel ON/OFF
    C/c = noise left scale up/down
    d = cycle plot decimation (1/2/4/8)
    j = save settings to flash
    J = load settings from flash
    v = print volumes

  Default boot mode: BOTH

  Future releases should migrate of driver/i2s.h

  Hardware Configuration of pre Amplifier.
  These are the options for components for the PCB microphone amplifier.
  R4,R8 and C5,C8
  Gain 17.5x: 82k   || 100pF v1 saturated
  Gain 12x:   56k   || 150pF
  Gain 10x:   47k   || 180pF v3 **
  Gain  2x:    8.2k || 1nF   v2 +/-6000 counts
  Amplifier designed as ~20kHz lowpass

*/

#include <Arduino.h>
#include <Wire.h>
#include <Adafruit_GFX.h>
#include <Adafruit_SSD1306.h>
#include <Adafruit_MPRLS.h>
#include "driver/rtc_io.h"
#include "driver/i2s.h"
#include "AudioBoard.h"
#include <Adafruit_MAX1704X.h>
#include <Preferences.h>
#include <math.h>

#define APP_VERSION 1.0
#define BAUDRATE 500000
char line[128];

// ===================== APP MODES =====================
#define APP_MODE_PRESSURE                  1
#define APP_MODE_STETHOSCOPE               2
#define APP_MODE_BOTH                      3
#define APP_MODE_NONE                      0

int appMode = APP_MODE_BOTH;   // default autonomous mode

// ===================== PIN MAP =====================
static const int MY_I2C_SDA    =         SDA;
static const int MY_I2C_SCL    =         SCL;
static const int MY_I2CSPEED   =      400000; // Clock Rate

static const int MY_ES8388ADDR =        0x10; // Address of ES8388 I2C port

static const gpio_num_t MY_BUTTON = GPIO_NUM_12; // Feather 12, Thing+ 9 active LOW

static const int MY_MPRLS_EOC  =          10; // Feather D10
static const int MY_MPRLS_RST  =          11; // Feather D11

static const int MY_I2S_MCLK   =          14; // Feather 14,   A4, Thing+ 13 Master Clock
static const int MY_I2S_BCLK   =          36; // Feather 36,  SCK, Thing+ 18 Bit Clock
static const int MY_I2S_LRCLK  =           8; // Feather  8,   A5, Thing+ 35 Left/Right Clock / Word Select
// Assembled with switched in/out
static const int MY_I2S_DOUT   =          37; // Feather 37, MISO, Thing+ 19 This is connected to DI on ES8388 (MISO)
static const int MY_I2S_DIN    =          35; // Feather 35, MOSI, Thing+ 23 This is connected to DO on ES8388 (MOSI)

#define STR_HELPER(x) #x
#define STR(x) STR_HELPER(x)

// ===================== OLED =====================
#define OLED_SCREEN_WIDTH                128
#define OLED_SCREEN_HEIGHT                32
#define OLED_RESET                        -1
#define OLED_ADDR                       0x3C
#define OLED_INTERVAL_MS                 200
#define BATTERY_INTERVAL_MS             5000

Adafruit_SSD1306 display(OLED_SCREEN_WIDTH, OLED_SCREEN_HEIGHT, &Wire, OLED_RESET);

// ===================== PRESSURE SENSOR =====================
// 1000 to 6.25 ms
#define MPRLS_INTERVAL_MS     100

Adafruit_MPRLS mpr(
  MY_MPRLS_RST, // RESET PIN
  MY_MPRLS_EOC, // EOC PIN
  0.0f,         // PSI_min
  300.0f,       // PSI_max
  2.5f,         // OUTPUT_min
  22.5f,        // OUTPUT_max
  1.0f          // PSI_to_HPA
);

bool          newPressure          =   false;
float         pressureZero         =    0.0f;
bool          pressureInitialized  =   false;
unsigned long awakeStartMs         =       0;
bool          autoShutoffTriggered =   false;


// ===================== ES8388 / I2S =====================
#define I2S_PORT                   I2S_NUM_0
// RATE_8k, RATE_11k, RATE_16k, RATE_22k,
// RATE_32k, RATE_44k, RATE_48k, RATE_64k,
// RATE_88k, RATE_96k, RATE_128k, RATE_176k, RATE_192k
#define AUDIO_SAMPLE_RATE           RATE_16K
#define AUDIO_DMA_BUF_LEN                128
#define AUDIO_DMA_BUF_COUNT                8
#define AUDIO_BLOCK_FRAMES               256
// CHANNELS2, CHANNELS9, CHANNELS16
#define AUDIO_NUM_CHANNELS         CHANNELS2
// BIT LENGTH_16BITS, BIT_LENGTH_18BITS
// BIT_LENGTH_20BITS, BIT_LENGTH_24BITS, BIT_LENGTH_32BITS
#define AUDIO_BIT_DEPTH    BIT_LENGTH_16BITS
#define AUDIO_ADC_IN         ADC_INPUT_LINE1
// DAC Output LINE1 (speaker)or LINE2 (headphone)
#define AUDIO_DAC_OUT       DAC_OUTPUT_LINE2

// Output: regValue = vol/3  -> 34 discrete levels (reg 0..33), 1.5 dB per step
// Vol step of 3 = 1 register step = 1.5 dB
#define AUDIO_OUTPUT_VOLUME               80
#define AUDIO_OUTPUT_VOLUME_STEP           6
// 0 to 100, internally it will map to 9 discrete levels
// Vol:   0,   13,  25,   38,   50,   63,   75,   88, 100
// dB:    0,    3,   6,    9,   12,   15,   18,   21,  24
// Power: 1,    2,   4,    8,   16,   32,   64,  128, 256  (power-of-2 per 3 dB step)
// Stepping is index-based (1 step = 3 dB) via stepInputVolume()
#define AUDIO_INPUT_VOLUME                75

// I2S_BITS_PER_SAMPLE_16BIT, I2S_BITS_PER_SAMPLE_24BIT
// I2S_BITS_PER_SAMPLE_32BIT;
#define AUDIO_I2S_BITS_PER_SAMPLE           I2S_BITS_PER_SAMPLE_16BIT

// ===================== DSP SETTINGS =====================
// Fixed DSP sample rate for coefficient calculations.
#define AUDIO_SAMPLE_RATE_HZ           16000.0f
#define HP_CUTOFF_MIN_HZ                   5.0f
#define HP_CUTOFF_MAX_HZ                  50.0f
#define HP_CUTOFF_DEFAULT_HZ              20.0f
#define LP_CUTOFF_MIN_HZ                1000.0f
#define LP_CUTOFF_MAX_HZ                4000.0f
#define LP_CUTOFF_DEFAULT_HZ            2000.0f
#define LP_STEP_HZ                       250.0f
#define HP_STEP_HZ                         1.0f
#define SW_GAIN_MIN                        0.5f
#define SW_GAIN_MAX                        4.0f
#define SW_GAIN_DEFAULT                    1.0f
#define SW_GAIN_STEP                       0.5f
#define NOISE_LEFT_SCALE_MIN               0.5f
#define NOISE_LEFT_SCALE_MAX               1.5f
#define NOISE_LEFT_SCALE_DEFAULT           1.0f
#define NOISE_LEFT_SCALE_STEP              0.05f
#define PLOT_DECIMATION_DEFAULT            4

int16_t audioBuffer[AUDIO_BLOCK_FRAMES * 2];
bool audioInitialized    =             false;
bool codecPinsConfigured =             false;

// Volumes
int outputVolume   =     AUDIO_OUTPUT_VOLUME;
int inputVolume    =      AUDIO_INPUT_VOLUME;

bool plotEnabled   =                   false;
int plotDecimation = PLOT_DECIMATION_DEFAULT;

bool  highPassEnabled    =             false;
bool  lowPassEnabled     =             false;
float highPassCutoffHz   =   HP_CUTOFF_DEFAULT_HZ;
float lowPassCutoffHz    =   LP_CUTOFF_DEFAULT_HZ;
float softwareGain       =   SW_GAIN_DEFAULT;
bool  noiseCancelEnabled =             false;
float noiseLeftScale     =   NOISE_LEFT_SCALE_DEFAULT;

float hpAlpha            =                 0.0f;
float lpAlpha            =                 0.0f;

struct ChannelFilterState {
  float hpXPrev;
  float hpYPrev;
  float lp1State;
  float lp2State;
};

ChannelFilterState leftFilterState  = {0.0f, 0.0f, 0.0f, 0.0f};
ChannelFilterState rightFilterState = {0.0f, 0.0f, 0.0f, 0.0f};

Adafruit_MAX17048 maxlipo;
bool batteryGaugeInitialized =           false;

Preferences appPrefs;

audio_driver::DriverPins codecPins;
AudioBoard               audioBoard(AudioDriverES8388, codecPins);
// ===================== TIMING =====================
unsigned long lastPressureMs =               0;
unsigned long lastOledMs     =               0;
unsigned long lastBatteryMs  =               0;

// ===================== DISPLAY STATE =====================
bool  updateOLED    =                    false;
float pressure_mmHg =                        0.0f;
float batteryPercent =                      -1.0f;

// ===================== HELPERS =====================
float clampf(float value, float minValue, float maxValue) {
  if (value < minValue) return minValue;
  if (value > maxValue) return maxValue;
  return value;
}

void saveAppSettings() {
  appPrefs.begin(   "mb-stetho", false);
  appPrefs.putInt(  "outVol",    outputVolume);
  appPrefs.putInt(  "inVol",     inputVolume);
  appPrefs.putFloat("swGain",    softwareGain);
  appPrefs.putBool( "hpEn",      highPassEnabled);
  appPrefs.putBool ("lpEn",      lowPassEnabled);
  appPrefs.putFloat("hpFc",      highPassCutoffHz);
  appPrefs.putFloat("lpFc",      lowPassCutoffHz);
  appPrefs.putBool( "ncEn",      noiseCancelEnabled);
  appPrefs.putFloat("ncScale",   noiseLeftScale);
  appPrefs.putInt(  "plotDecim", plotDecimation);
  appPrefs.end();
}

void loadAppSettings() {
  appPrefs.begin("mb-stetho", true);
  outputVolume       = appPrefs.getInt(  "outVol",  AUDIO_OUTPUT_VOLUME);
  inputVolume        = appPrefs.getInt(  "inVol",   AUDIO_INPUT_VOLUME);
  softwareGain       = appPrefs.getFloat("swGain",  SW_GAIN_DEFAULT);
  highPassEnabled    = appPrefs.getBool( "hpEn",    false);
  lowPassEnabled     = appPrefs.getBool( "lpEn",    false);
  highPassCutoffHz   = appPrefs.getFloat("hpFc",    HP_CUTOFF_DEFAULT_HZ);
  lowPassCutoffHz    = appPrefs.getFloat("lpFc",    LP_CUTOFF_DEFAULT_HZ);
  noiseCancelEnabled = appPrefs.getBool( "ncEn",    false);
  noiseLeftScale     = appPrefs.getFloat("ncScale", NOISE_LEFT_SCALE_DEFAULT);
  plotDecimation     = appPrefs.getInt(  "plotDecim", PLOT_DECIMATION_DEFAULT);
  appPrefs.end();

  outputVolume   = (int)clampf((float)outputVolume, 0.0f, 100.0f);
  inputVolume    = (int)clampf((float)inputVolume, 0.0f, 100.0f);
  softwareGain   = clampf(softwareGain, SW_GAIN_MIN, SW_GAIN_MAX);
  noiseLeftScale = clampf(noiseLeftScale, NOISE_LEFT_SCALE_MIN, NOISE_LEFT_SCALE_MAX);
  if (plotDecimation != 1 && plotDecimation != 2 &&
      plotDecimation != 4 && plotDecimation != 8) plotDecimation = PLOT_DECIMATION_DEFAULT;
}

// Audio filtering functions:
// high-pass and low-pass filters
// software gain
//
// High-pass 1st order IIR filter
// Low-pass 2 cascaded first order IIR filters (2 pole Low-pass)

void updateFilterCoefficients() {
  highPassCutoffHz = clampf(highPassCutoffHz, HP_CUTOFF_MIN_HZ, HP_CUTOFF_MAX_HZ);
  lowPassCutoffHz  = clampf(lowPassCutoffHz, LP_CUTOFF_MIN_HZ, LP_CUTOFF_MAX_HZ);

  float hpRC = 1.0f / (2.0f * PI * highPassCutoffHz);
  float hpDt = 1.0f / AUDIO_SAMPLE_RATE_HZ;
  hpAlpha = hpRC / (hpRC + hpDt);

  float lpRC = 1.0f / (2.0f * PI * lowPassCutoffHz);
  float lpDt = 1.0f / AUDIO_SAMPLE_RATE_HZ;
  lpAlpha = lpDt / (lpRC + lpDt);
}

float applyAudioFilters(float inputSample, ChannelFilterState &state) {
  float x = inputSample;

  if (highPassEnabled) {
    float y = hpAlpha * (state.hpYPrev + x - state.hpXPrev);
    state.hpXPrev = x;
    state.hpYPrev = y;
    x = y;
  }

  x *= softwareGain;

  if (lowPassEnabled) {
    state.lp1State += lpAlpha * (x - state.lp1State);
    state.lp2State += lpAlpha * (state.lp1State - state.lp2State);
    x = state.lp2State;
  }

  return x;
}

void printAudioFilterStatus() {
  Serial.println("Audio processing:");
  snprintf(line, sizeof(line), "  %-20s = %6.2f",                    "SW gain",            softwareGain);
  Serial.println(line);
  snprintf(line, sizeof(line), "  %-20s = %-3s @ %6.1f Hz",          "HP filter",          highPassEnabled ? "ON" : "OFF", highPassCutoffHz);
  Serial.println(line);
  snprintf(line, sizeof(line), "  %-20s = %-3s @ %6.1f Hz",          "LP filter",          lowPassEnabled ? "ON" : "OFF", lowPassCutoffHz);
  Serial.println(line);
  snprintf(line, sizeof(line), "  %-20s = %-3s, left scale = %5.2f", "Noise cancel (R-L)", noiseCancelEnabled ? "ON" : "OFF", noiseLeftScale);
  Serial.println(line);
  snprintf(line, sizeof(line), "  %-20s = %d",                       "Plot decimation",    plotDecimation);
  Serial.println(line);
  Serial.println("=========================================================");
}
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

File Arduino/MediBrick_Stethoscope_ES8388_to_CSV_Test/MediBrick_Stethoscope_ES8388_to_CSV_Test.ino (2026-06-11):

/**
 * Read two microphones, Output to  CSV, Change Microphone Volume up and down
 * @author Urs Utzinger
 * @copyright GPLv3 
 * USE SPAKRFUN TINRPLUS C
 **/

#include "Arduino.h"
#include "AudioTools.h"
#include "AudioTools/AudioLibs/I2SCodecStream.h"
#include "logger.h"

#define BAUDRATE 500000

#define SAMPLE_RATE           RATE_16K // 8k, 11k, 16k, 22k, 32k, 44k
#define NUM_CHANNELS         CHANNELS2
#define BIT_DEPTH    BIT_LENGTH_16BITS
#define ADC_IN         ADC_INPUT_LINE1

#define INPUT_VOLUME        1 // 0..100 (not linear)

// I2C
#define SDAPIN             SDA // I2C Data,  Adafruit ESP32 S3 3, Sparkfun Thing Plus C 23
#define SCLPIN             SCL // I2C Clock, Adafruit ESP32 S3 4, Sparkfun Thing Plus C 22
#define I2CSPEED        400000 // Clock Rate
#define ES8388ADDR        0x10 // Address of ES8388 I2C port

// I2S, your configuration for the ES8388 board
#define MCLKPIN             A4 // Master Clock
#define BCLKPIN            SCK // Bit Clock
#define WSPIN               A5 // Word select
#define DOPIN             MISO // This is connected to DI on ES8388 (MISO)
#define DIPIN             MOSI // This is connected to DO on ES8388 (MOSI)


uint16_t toSamplingFreq(samplerate_t rate) {
    switch (rate) {
        case RATE_8K:   return   8000;
        case RATE_11K:  return  11025;
        case RATE_16K:  return  16000;
        case RATE_22K:  return  22050;
        case RATE_24K:  return  24000;
        case RATE_32K:  return  32000;
        case RATE_44K:  return  44100;
        case RATE_48K:  return  48000;
        case RATE_64K:  return  64000;
        case RATE_88K:  return  88200;
        case RATE_96K:  return  96000;
        case RATE_128K: return 128000;
        case RATE_176K: return 176400;
        case RATE_192K: return 192000;
        default:        return -1;  // Handle error for unknown rate
    }
}

uint8_t toBitDepth(sample_bits_t bits) {
    switch (bits) {
        case BIT_LENGTH_16BITS: return 16;
        case BIT_LENGTH_18BITS: return 18;
        case BIT_LENGTH_20BITS: return 20;
        case BIT_LENGTH_24BITS: return 24;
        case BIT_LENGTH_32BITS: return 32;
        default:                return -1;  // Handle error for unknown bit length
    }
}

uint16_t toNumChannels(channels_t channels) {
    switch (channels) {
        case CHANNELS2:  return  2;
        case CHANNELS8:  return  8;
        case CHANNELS16: return 16;
        default:         return -1;  // Handle error for unknown number of channels
    }
}

uint16_t sample_rate  =  toSamplingFreq(SAMPLE_RATE);
uint8_t bit_depth     =  toBitDepth(BIT_DEPTH);
uint16_t num_channels =  toNumChannels(NUM_CHANNELS);

AudioInfo           info_i2s_in(    sample_rate, num_channels, bit_depth);
AudioInfo           info_serial_out(sample_rate, num_channels, bit_depth);
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

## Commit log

2026-04-28 Update assembly.md: hot air soldering
    Added instructions for hot-air pressure sensor soldering.
2026-04-28 Update assembly.md
    Updated electronic assembly section.
2026-04-28 Add link for pressure sensor.
2026-04-28 Update assembly.md
    Cleared up 3D printing wording.
2026-04-29 Update README.md: Microphone Assembly
2026-05-07 Update assembly.md for ALL instructions
2026-06-11 Remove vendored libraries and update docs for external dependencies
    [Sound_BOM_2024.xlsx, Sound_BOM_2026.xlsx]
2026-06-14 Add KiCad PCB design and enhance firmware
    [DDF0008A.stl, DDF0008A.stp, ES8388.step, MPRLS0300YG00001B_HNW.step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]

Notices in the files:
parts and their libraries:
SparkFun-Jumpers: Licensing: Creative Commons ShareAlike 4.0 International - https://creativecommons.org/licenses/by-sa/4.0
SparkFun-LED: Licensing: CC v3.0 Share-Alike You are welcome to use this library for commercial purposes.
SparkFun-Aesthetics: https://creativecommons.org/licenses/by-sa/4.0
